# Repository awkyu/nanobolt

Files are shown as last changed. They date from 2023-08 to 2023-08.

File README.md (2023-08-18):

# nanobolt
This project is a proposal for the design of an ablation probe for osteoid osteoma using a new ablation technique proposed by Pavitra Krishnaswamy, Andras Kuthi, P. Thomas Vernier, and Martin A. Gundersen [[1]](https://doi.org/10.1109/TDEI.2007.4286518).

Surgical resection and thermal ablation techniques have been shown to have suboptimal efficacy for the treatment of osteoid osteomas due to the high risk of complications and large ablation zones. Ablation technologies that utilize electric fields instead of thermal energy to produce nanosized pores in tumor cell membranes have been shown to be an attractive method for treating a wide variety of cancers due to the short ablation times and non-invasive nature of the procedure. We propose a nanosecond pulse electric field ablation system utilizing a pulse generator as a compact solution to ablate osteoid osteomas without harming the healthy bone, leading to reduced instances of post-operative complications. 

[1] P. Krishnaswamy, A. Kuthi, P. T. Vernier and M. A. Gundersen, "Compact Subnanosecond Pulse Generator Using Avalanche Transistors for Cell Electroperturbation Studies," IEEE Transactions on Dielectrics and Electrical Insulation, vol. 14, no. 4, pp. 873-877, Aug. 2007, doi: 10.1109/TDEI.2007.4286518.

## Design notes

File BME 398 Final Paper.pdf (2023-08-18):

Abstract — Surgical resection and thermal ablation techniques have been shown to have suboptimal efficacy for the treatment of osteoid osteomas due to the high risk of complications and large ablation zones. Ablation technologies that utilize electric fields instead of thermal energy to produce nanosized pores in tumor cell membranes have been shown to be an attractive method for treating a wide variety of cancers due to the short ablation times and noninvasive nature of the procedure. We propose a nanosecond pulse electric field ablation system utilizing a pulse generator as a compact solution to ablate osteoid osteomas without harming the healthy bone, leading to reduced instances of post-operative complications.

Clinical Relevance — This establishes the efficacy of nanosecond pulse electric field ablation to ensure complete nidus ablation.

INTRODUCTION
Osteoid osteomas are small, benign bone tumors typically found in adolescents that cause pain and discomfort. The standard of care for treating osteoid osteomas has been surgical resection. Although surgical resection has been shown to have success rates of 88%-97% in removing osteoid osteomas, these procedures have a high rate of complications (20-45%) including hematoma, infection, and avascular necrosis [0, 1]. Additionally, surgically induced bone defects can increase the risk of fracture [2, 3, 4].

Minimally-invasive ablation techniques have been implemented to treat osteoid osteomas, as these techniques have been proven to cause fewer postoperative complications than conventional surgical excision [2]. Currently, radiofrequency ablation is the most common thermal ablation treatment for osteoid osteomas due to its wide availability, short postprocedural hospitalization, and ablation zone of 3-4cm [2]. Alternatively, microwave ablation has been shown to have faster ablation time and deeper tissue penetration. This is not without drawbacks. With the average nidus size of approximately 1 cm, the microwave ablation zone of 5-7 cm poses the risk of causing thermal damage to non-target tissues. This collateral damage proves to be a major drawback of microwave ablation for the treatment of osteoid osteoma [2]. In a preliminary study, Fan et al. used microwave ablation for the treatment of malignant bone tumors with a 74% success rate [5]. However, complications such as fracture, local recurrence, and infection still arose in the study, likely due to thermal damage to the surrounding healthy tissue. While radiofrequency and microwave ablation have various benefits for treating osteoid osteomas, other energy types may provide these same benefits of ablation time and tissue penetration while also limiting the ablation zone.

More recently, non-thermal ablation technologies have been investigated for tumor ablation that utilize electric fields rather than thermal energy. Irreversible electroporation (IRE) delivers low electric fields (low kV/cm) in pulses with durations of milliseconds or microseconds. The electric energy creates pores in the cell membranes of the tumor cells which disrupts ionic gradients, eventually causing the cell to die from necrosis [6]. Nanosecond pulse electric field (nsPEF) ablation uses a similar technique but with higher electric fields (tens of kV/cm) with a
nanosecond duration. The advantage of nsPEF ablation over IRE is that nsPEF ablation creates pores in both the plasma membranes as well as intracellular membranes, resulting in a phenomenon known as supra-electroporation [6]. Several studies have shown how this supra-electroporation leads to the induction of apoptosis and DNA damage [6, 7, 8]. Compared to other ablation techniques, nsPEF ablation is more time-efficient as only 100 pulses are needed to effectively destroy the tumor [6, 7]. The ability of nsPEF to rapidly induce cell death noninvasively without the use of heat or chemicals makes it an attractive treatment option for a plethora of cancers.

While the literature has shown that nsPEF ablation has been successful in treating a variety of tumors, it has not been extensively researched for the ablation of osteoid osteoma. This study aims to address this gap in knowledge and proposes a nanosecond pulse generator that will be used to induce supra-electroporation in osteoid osteomas. The nanosecond pulse generator will be used in combination with a custom probe, and both of these components will comprise the entire nanosecond pulse electric field ablation system. By using a novel power generator, this solution will target osteoid osteomas with more precision, limiting collateral damage to surrounding bone or tissue.

For this preliminary study, only the pulse generator was verified as the probe design is still being perfected. Testing the new nanosecond pulse generator in silico using Multisim software demonstrates a pulse with a magnitude of approximately 2 V is produced. While other nanosecond pulse generators can produce pulses with a voltage greater than 1 kV, this study still offers verification that the simplified circuit used in this study produces pulses of electrical energy. This provides the confidence needed to further develop the project by building upon the current circuit design to achieve the voltages required for effective ablation. Future studies should be conducted to further verify the circuit design as well as the probe before validating the entire ablation system by assessing its feasibility in vivo for the removal of osteoid osteomas. METHODS

Multisim software was used to simulate the circuit needed for the nanosecond pulse generator. In a paper published by Krishnaswamy et al., a detailed schematic is provided for an avalanche pulse generator circuit which served as the inspiration for this study [9]. Using the avalanche pulse generator circuit as a starting point, this study aimed to first simulate the findings of Krishnaswamy et al., and then alter key parameters to change the output characteristics of the circuit. The circuit model used in the Multisim simulation was assembled as seen in figure 1. The DC power supply block, which consisted of a 8-14.5 VDC power supply followed by a DC-DC converter, was simplified as a 2.5 kV voltage source in the simulation. The transformer was modeled with no leakage inductance or resistance; the core was modeled as non-ideal with a flux of 250uWb * tanh(.2*i) where “i” was the magnetizing inductance current. The Bipolar Junction Transistor (BJT) NPN transistor was used to model the avalanche transistor. This transistor provided a conservative estimate of the circuit as it lacked the quick response of the avalanche transistors. The rise time of the trigger source was specified as 0.5 nanoseconds and varying levels of voltages were applied to assess the impact of the voltage on the output waveform. Peak voltage and rise time of the waveform were analyzed using a transient analysis with a step time of 0.1 nanoseconds.

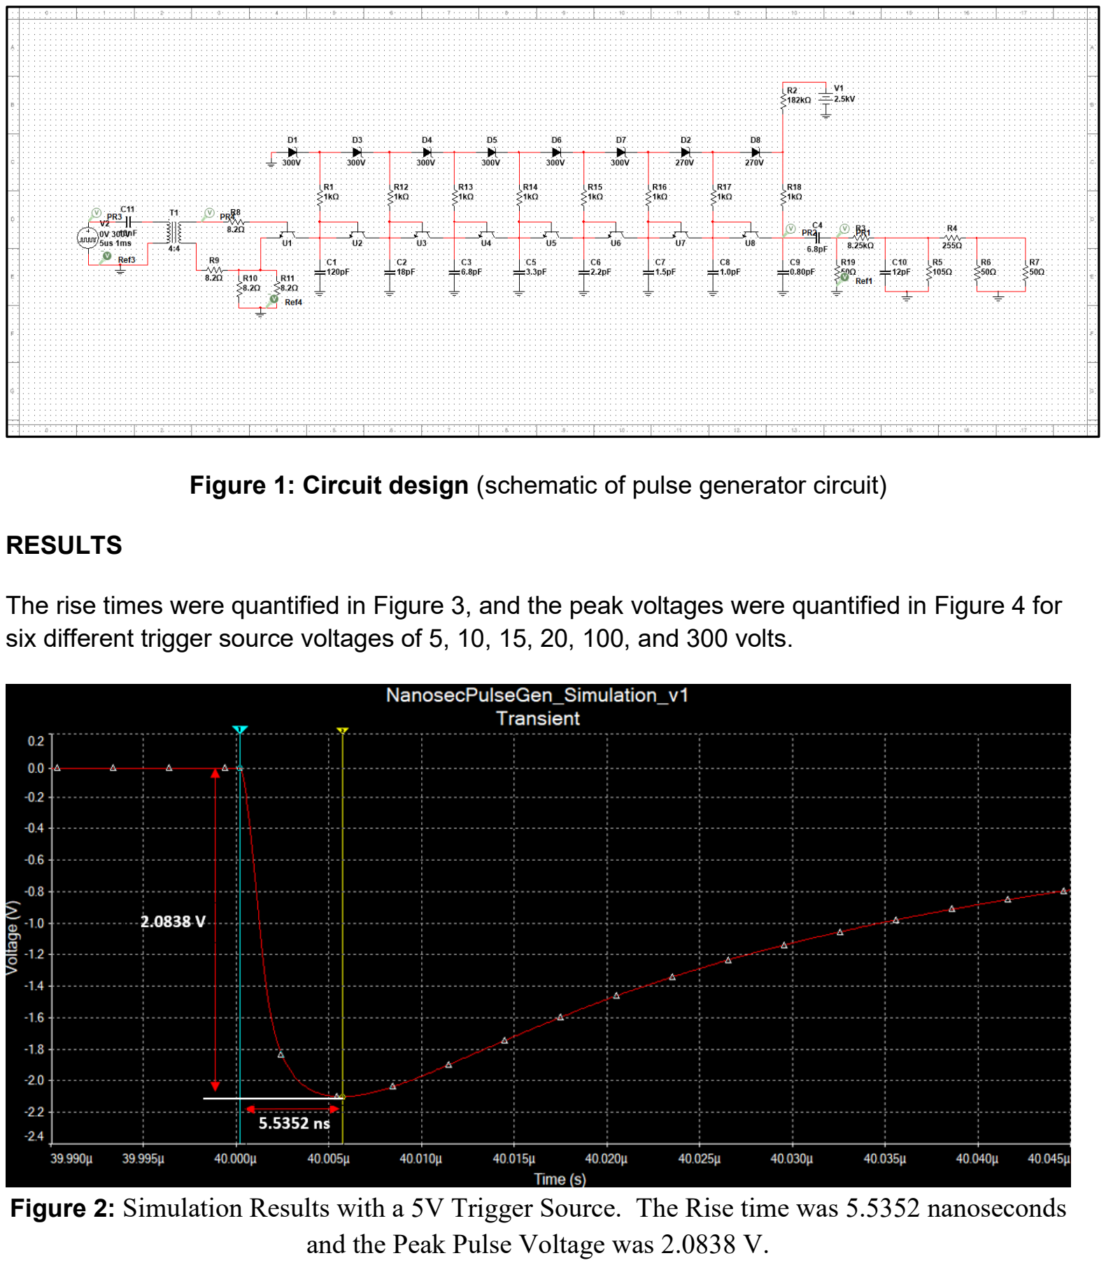
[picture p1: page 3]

Figure 1: Circuit design (schematic of pulse generator circuit) RESULTS

The rise times were quantified in Figure 3, and the peak voltages were quantified in Figure 4 for six different trigger source voltages of 5, 10, 15, 20, 100, and 300 volts.

Figure 2: Simulation Results with a 5V Trigger Source. The Rise time was 5.5352 nanoseconds and the Peak Pulse Voltage was 2.0838 V.

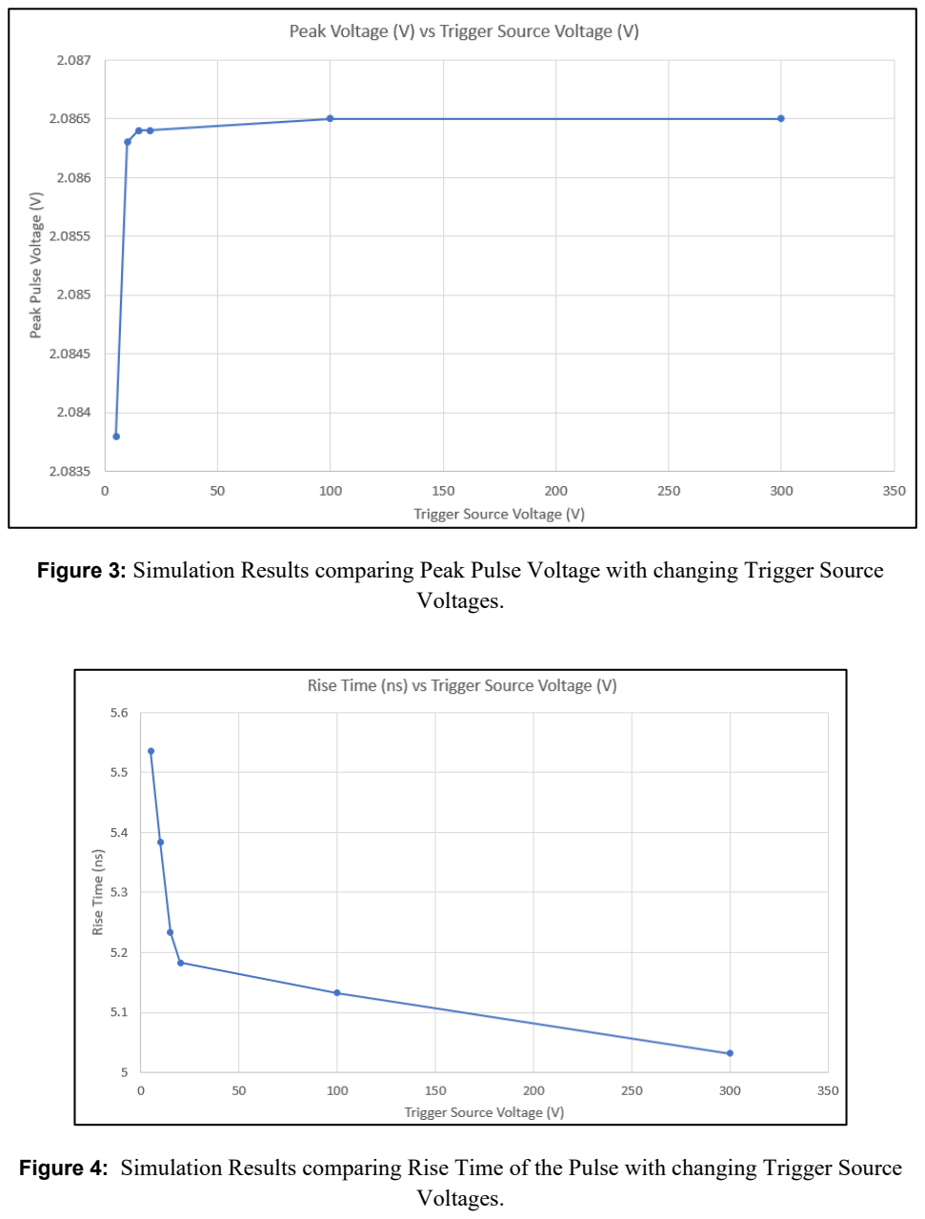
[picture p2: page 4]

Figure 3: Simulation Results comparing Peak Pulse Voltage with changing Trigger Source Voltages.

Figure 4: Simulation Results comparing Rise Time of the Pulse with changing Trigger Source Voltages.

DISCUSSION

In Figure 2, the output signal was shown in the time-domain with a single trigger source voltage of 5 volts. This output signal showed promising results in that it had the shape of a pulse that could be used in electroporation applications. However, the voltage magnitude was roughly a thousandth of the desired value [9]. This decreased magnitude would render the device useless in electroporation applications. However, further modification of the simulation could lead to a more appropriate waveform for the generator’s intended use. Additionally, a prototype of the generator could be assembled and the output voltage could be assessed to compare results with the simulation. While this would have a cost associated with it, the testing may reveal limitations of the Multisim simulation software.

According to Figure 3, the peak voltage approached a horizontal asymptote at around 2 volts with an increasing trigger source voltage. These peak voltage values deviated from normal kilovolt values for the peak voltage in similar ablation technologies by orders of magnitude. On the other hand, rise times of around 5 nanoseconds (see Figure 4) were very plausible and much lower than millisecond to microsecond rise times in similar technologies. In order to improve the rise times to the subnanosecond range in future simulations, avalanche transistors could be used instead of ideal transistors.

There were a number of limitations in this study that hindered the results. First, this study was restricted to a simulated environment, which idealized many components to a form that was not indicative of their real-world state. Second, this study was limited to a short 15-week period of clinical research, needs statement identification and selection, finally followed with experimental design and performance. With additional time in the future, this study would be able to put together a real world model of the pulse generator.

Although this study found rather low peak pulse voltages, the overall nature of these pulses still offered verification for the treatment of osteoid osteomas with nanosecond pulse electric field ablation technologies. This study was able to produce pulses with short rise times, which was a key waveform characteristic when evaluating a pulse generator for its capability of treating osteoid osteomas via ablation.
CONCLUSION

This study aimed to test a new nanosecond pulse generator in silico with Multisim software to produce a pulse capable of powering an ablation probe utilizing a simplified circuit design. Although the resulting voltage magnitude was approximately a thousandth of the desired value, the output signal had the shape of a signal used in electroporation applications. With further modification of the schematic design of the circuit, the design shows promise in achieving a desirable waveform for the intended application. A prototype of the generator could also be fabricated and further tested to analyze the output voltage. This testing would reveal and mitigate the limitations of the in silico experiment. In addition to the verification of the variability in power of the circuit design, future studies could focus on the verification and validation of the efficiency of the circuit. Using Multisim or electromagnetic simulation, the circuit could be modified to operate between 915 MHz and 2450 MHz in order to have an ablation time of less than 10 minutes. The results of this study provides confidence in accurate modification of the circuit design to produce desired output signals and pulse magnitudes for use in the treatment of osteoid osteomas. Future studies should test the pulse generator with the ablation probe on an ex vivo tissue sample to analyze the effectiveness of the ablation technology on osteoid osteomas.

References

[0] C. Neyisci, Y. Erdem, “Safe and Effective Treatment Choice for Osteoid Osteoma: Computed Tomography-guided Percutaneous Radiofrequency Ablation,” Cureus vol. 11, no. 8. pp. e5526, Aug. 2019. Accessed on: Apr. 21, 2021. [Online]. Available doi: 10.7759/cureus.5526
[1] Y. Oc, B. E. Kilinc, S. Cennet, M. M. Boyacioglu, R. Ertugrul, and A. Varol, “Complications of Computer Tomography Assisted Radiofrequency Ablation in the Treatment of Osteoid Osteoma,” BioMed Research International, vol. 2019, pp. 1–6, May 2019, doi: 10.1155/2019/4376851.
[2] “Thermal Ablation of Osteoid Osteoma: Overview and Step-by-Step Guide,” RadioGraphics, vol. 29, pp. 2127-2141, Nov. 2009. Accessed on: Mar. 3, 2021. [Online]. Available doi: 10.1148/rg.297095081
[3] D. I. Rosenthal, F. J. Hornicek, M. W. Wolfe, L. C. Jennings, M. C. Gebhardt, H. J. Mankin, “Percutaneous Radiofrequency Coagulation of Osteoid Osteoma Compared with Operative Treatment,” The Journal of Bone and Joint Surgery, vol. 80, no. 6, pp. 815-821, June 1998. Accessed on: Mar. 7, 2021. [Online]. Available doi: 10.2106/00004623-199806000-00005
[4] Z. G. Papathanassiou, P. Megas, T. Petsas, D. J. Papachristou, J. Nilas, D. Siablis, “Osteoid Osteoma: Diagnosis and Treatment,” Orthopedics, vol. 11, no. 31, pp. 1118-1127, Nov. 2008. Accessed on: Mar. 7, 2021. [Online]. Available doi: 10.3928/01477447-20081101-20
[5] Q. Fan, B. Ma, Y. Zhou, M. Zhang, X. Hao, “Bone tumors of the extremities or pelvis treated by microwave-induced hyperthermia,” Clinical orthopaedics and related research, no. 406, 2015. Accessed on: Mar. 7, 2021. [Online]. Available doi: 10.1097/01.blo.0000037439.23683.9c
[6] S. Beebe, N. Sain, and W. Ren, “Induction of Cell Death Mechanisms and Apoptosis by Nanosecond Pulsed Electric Fields (nsPEFs),” Cells, vol. 2, no. 1, pp. 136–162, Mar. 2013, doi: 10.3390/cells2010136.
[7] X. Chen, J. F. Kolb, R. J. Swanson, K. H. Schoenbach, and S. J. Beebe, “Apoptosis initiation and angiogenesis inhibition: melanoma targets for nanosecond pulsed electric fields,” Pigment Cell & Melanoma Research, vol. 23, no. 4, pp. 554–563, Apr. 2010, doi: 10.1111/j.1755-148x.2010.00704.x.
[8] T. Koga, K. Morotomi-Yano, T. Sakugawa, H. Saitoh, and K. Yano, “Nanosecond pulsed electric fields induce extracellular release of chromosomal DNA and histone citrullination in neutrophil-differentiated HL-60 cells,” Scientific Reports, vol. 9, no. 1, Jun. 2019, doi: 10.1038/s41598-019-44817-9.
[9] P. Krishnaswamy, A. Kuthi, P. T. Vernier and M. A. Gundersen, "Compact Subnanosecond Pulse Generator Using Avalanche Transistors for Cell Electroperturbation Studies," IEEE Transactions on Dielectrics and Electrical Insulation, vol. 14, no. 4, pp. 873-877, Aug. 2007, doi: 10.1109/TDEI.2007.4286518.

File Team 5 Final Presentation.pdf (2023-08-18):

# REdesign Lab

# Team 5: NanoBolt™

# Bevin Neill, Jefferson Bercaw, Mattie Mckee, Alex Kyu, and Drew DiSerafino

# Clinical Problem

# - Osteoid Osteomas

# - Small benign bone tumors - Typically affect children and young adults - Account for 11% of all benign bone tumors (~450,000 cases per year) - Cause pain and discomfort

# - Current Solutions

# - Surgical Resection

# - High risk of complications - Increased risk of fracture

# - Thermal Ablation

# - Microwave or radiofrequency - Ablation zone size of 5-7 cm - Average size of osteoid osteoma = 1-2 cm - Increased risk of damage to healthy bone

https://www.youtube.com/watch?v=gGn3XhZBSQA

https://www.jnjmedicaldevices.com/en-US/product-family/neuwave-microwave-ablation-systems

A. Julka, P. Jebson, and M. Tomaino, “Common Benign Tumors of the Hand,” AAOS, Aug. 2015. https://www5.aaos.org/OKOJ/vol13/issue8/HAN055/?ssopc=1

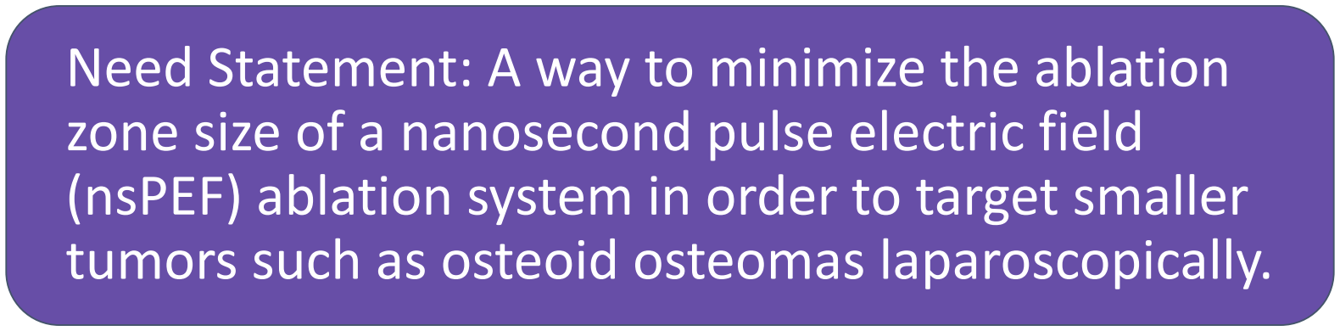
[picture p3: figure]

# Need Statement: A way to minimize the ablation zone size of a nanosecond pulse electric field (nsPEF) ablation system in order to target smaller

tumors such as osteoid osteomas laparoscopically.

# Lab Market and FDA Regulation

# TAM: Total US Bone Tumor Population

# SAM: Benign bone tumor cases

# Target: Osteoid osteoma cases

# Market Size: ~450,000 * $1,940/patient = $873,000,000

# Value Proposition: Lower Ablation Zone and novel application

# Product Code: NEY

# Regulation Number: 878.4400

# Regulatory Pathway: Class 2, 510(k)

# Estimated Individuals with Bone Tumors Population in US

(18,150,000 = ~5.5%)

# Malignant tumors

~77.1%

# Benign bone tumors

(4,148,571 = ~22.9%)

# Osteoid osteoma

11% or 456,342

G. R. Gaumer, D. S. Weinberg, C. D. Collier, P. J. Getty, and R. W. Liu, “An Osteological Study on the Prevalence of Osteochondromas,” The Iowa orthopaedic journal, vol. 37, pp. 147–150, 2017, Accessed: Feb. 23, 2021. [Online]. Available: https://www.ncbi.nlm.nih.gov/pmc/articles/PMC5508295/
S. Noordin et al., “Osteoid osteoma: Contemporary management,” Orthopedic Reviews, vol. 10, no. 3, Sep. 2018, doi: 10.4081/or.2018.7496.
S. A. Astani, M. L. Brown, and K. Steusloff, “Comparison of Procedure Costs of Various Percutaneous Tumor Ablation Modalities,” The Association for Medical Imaging Management, Aug 2014, Accessed: Feb. 23, 2021. [Online]. Available: http://www.ahra.org/AM/Downloads/OI/qc/RM364_p12-17_Features.pdf

# Traceability Matrix

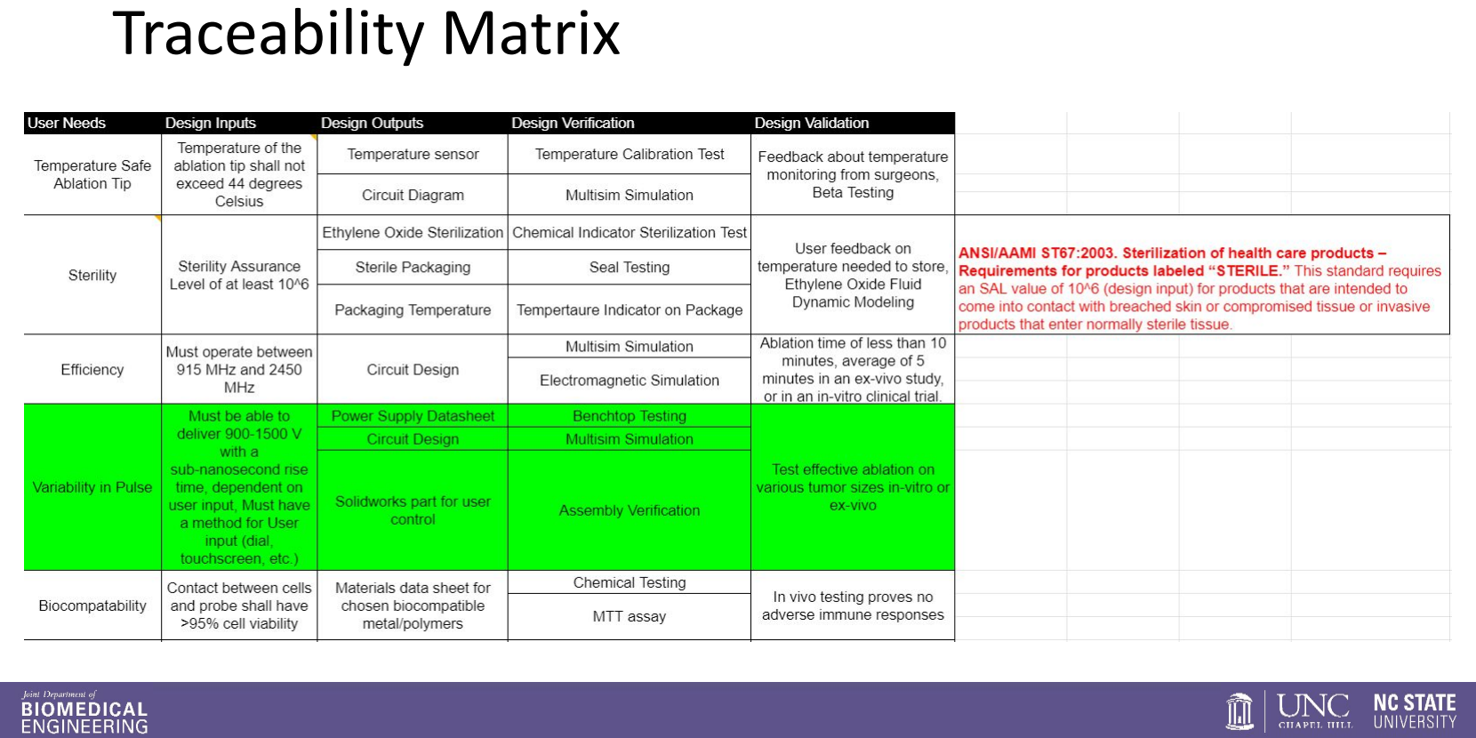
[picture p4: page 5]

# Traceability Matrix (Continued)

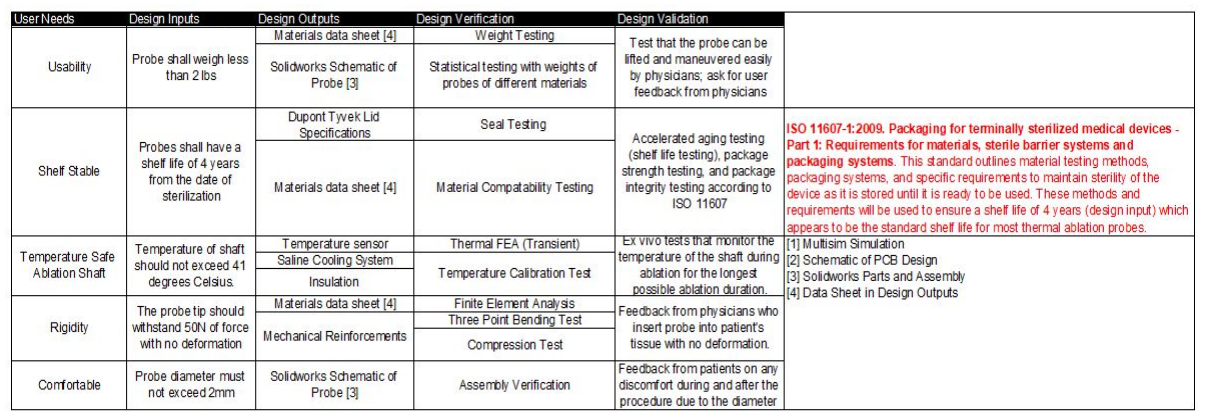
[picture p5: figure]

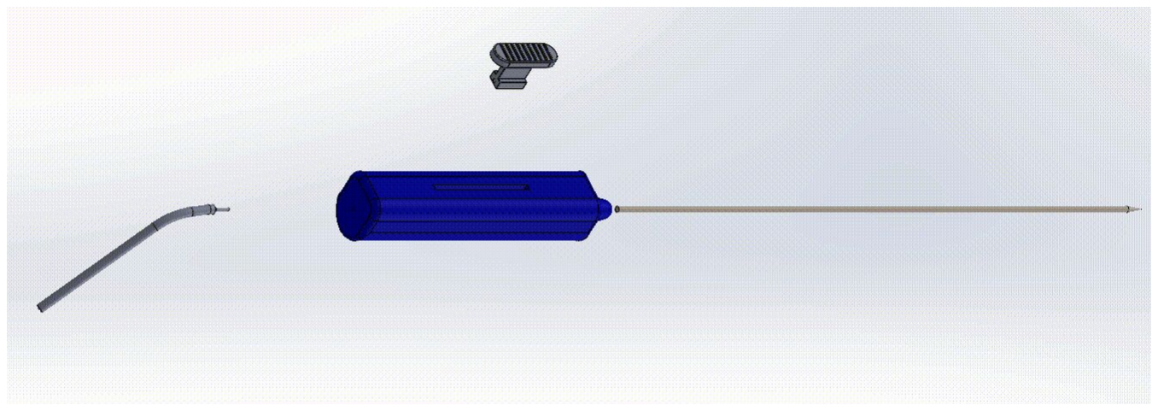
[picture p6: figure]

# Solution

# - Nanosecond Pulse Electric Field (nsPEF) Ablation

# - High-intensity pulsed electric fields with a nanosecond pulse duration - Creates pores in both the plasma membrane and intracellular membrane

# - Induce apoptosis in tumor cells

# - Subnanosecond Pulse Generator - creates pulses of electrical energy - Probe - application of electric field to tumor - Thumb Tab - control depth of insertion - Insulator - protect surrounding tissue

| Component | Cost
PCB Materials* | $ 420.33
Metal Probe | $ 6.99
Thumb Tab | $ 9.99
Handle | $ 9.99
Custom Wire | $ 6.99
Insulator | $ 17.99
Total | $ 472.28

# Bill of Materials

# * see Appendix A

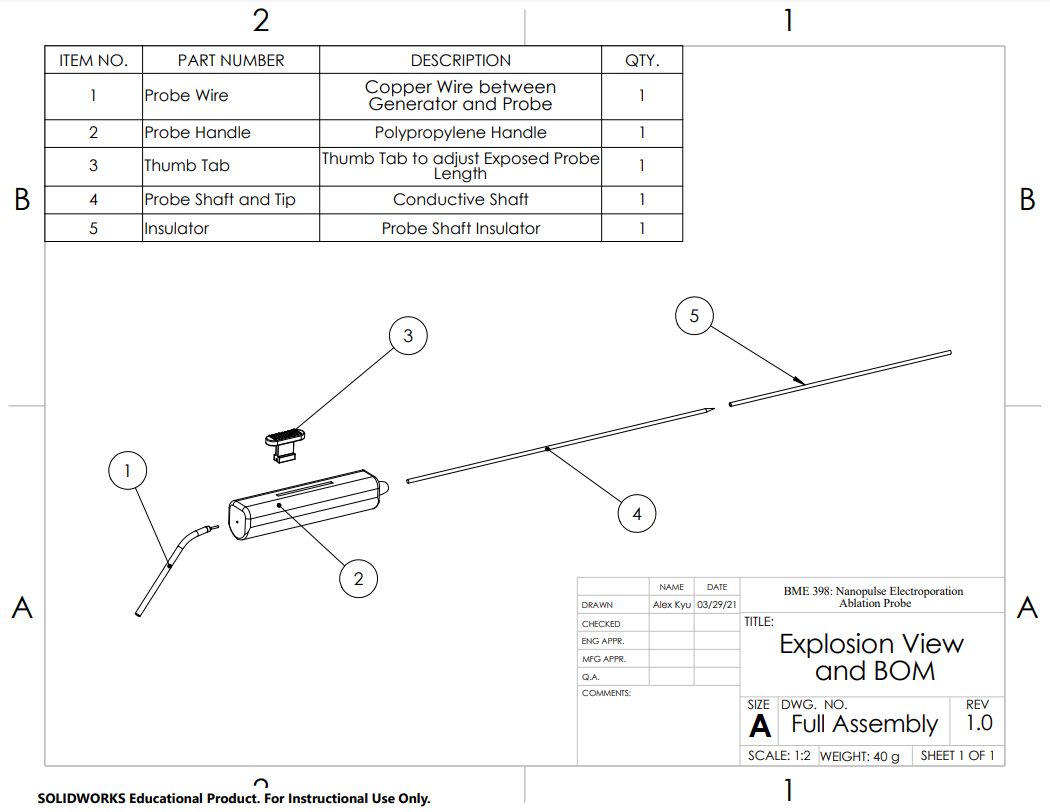
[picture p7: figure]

# Lab Manufacturing Methods

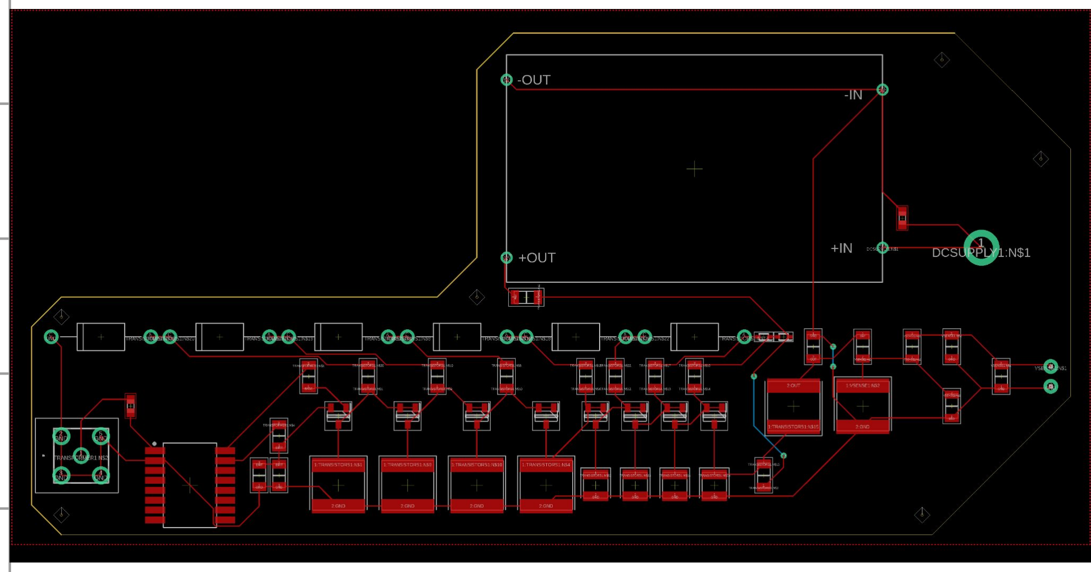
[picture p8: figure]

Part | Supplier/Manufacturer | Material
Plastic Handle | Injection Molding | Polypropylene
Insulator | Insulon® Sheaths | Stainless Steel
Probe | Lathe | Stainless Steel
Wire | Y.C. Cable® | Multiple

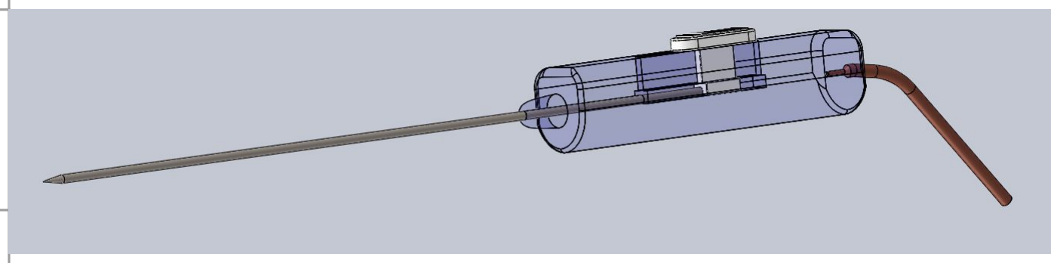
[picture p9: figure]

Thumb Probe Adjustor | Injection Molding | Polypropylene
Generator | JLCPCB® | PCB

# DFM Principles

# Principles used in our design:

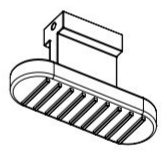
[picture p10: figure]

# a. Largest Acceptable Tolerances (outer portion of handle) b. Available Manufacturing Techniques in the Fab Lab c. Geometry (Cylinders!) Possible areas of improvement: a. Poka Yoke (Thumb Tab) b. Singular Axis of Assembly (Divide handle)

# Verification/Validation

# Multisim Simulation of Power Generator Circuit

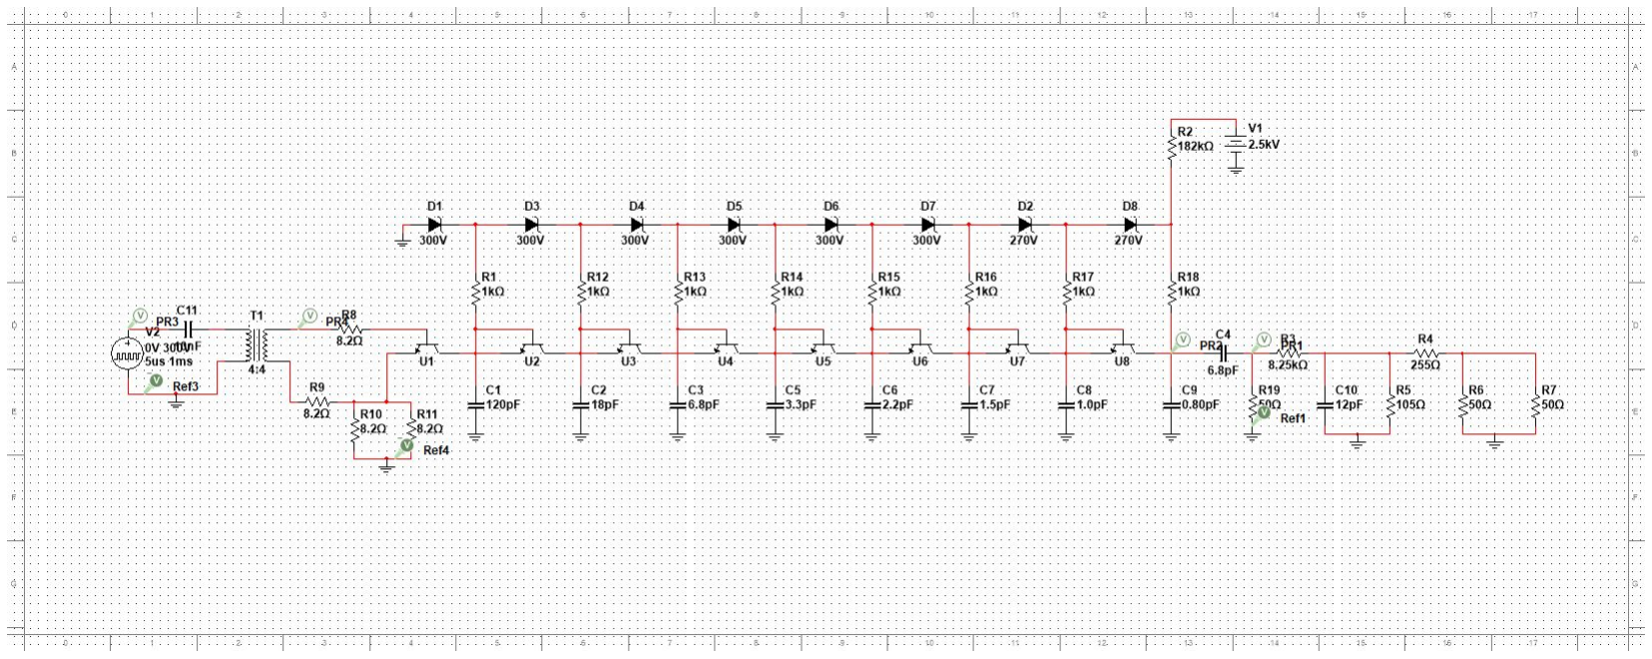
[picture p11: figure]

T. Koga, K. Morotomi-Yano, T. Sakugawa, H. Saitoh, and K. Yano, “Nanosecond pulsed electric fields induce extracellular release of chromosomal DNA and histone citrullination in neutrophil-differentiated HL-60 cells,” Scientific Reports, vol. 9, no. 1, Jun. 2019, doi: 10.1038/s41598-019-44817-9.

# Verification/Validation

# User Need: Variability in Pulse time

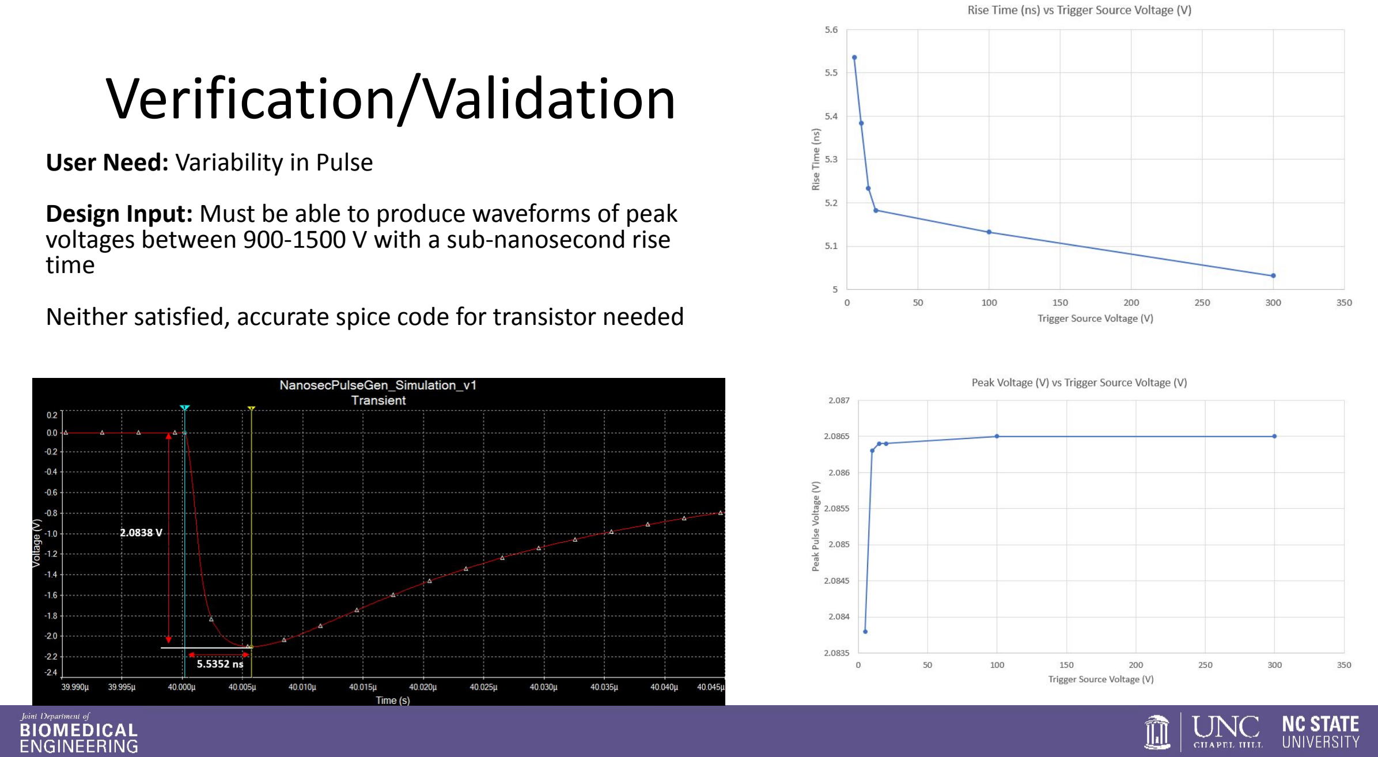
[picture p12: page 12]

# Design Input: Must be able to produce waveforms of peak voltages between 900-1500 V with a sub-nanosecond rise

# Neither satisfied, accurate spice code for transistor needed

# Project Analysis and Future

# - Future studies:

# - Prototype generator to analyze output voltage - Test the pulse generator with the ablation probe on an ex vivo tissue sample - Will likely need to raise additional funds for project (estimated prototype cost

$472.28)

# - Timeline is achievable, although will be tight

# - Risks

# - Overall Success

# - Generator not producing desired output waveform - Financial Risk: expensive prototype

# - User Harms

# - Leakage Current - Electric Field produced too large - Detached thumb tab - Misinterpretation of user interface to set ablation power

# - Continuing For Senior Design

# - Solution meets unmet clinical need with a large market size - Design is feasible to manufacture, especially using Fab Lab

# Questions?

Appendix A - Full PCB BOM Part Name | Unique Identifying Number | Description | Quantity | Material | Vendor | Unit Cost | Total Cost
Avalanche Transistor | TR1 | Avalanche Transistor | 8 | n/a | Mouser | $9.73 | $77.84
DC-DC Converter | CONV1 | DC-DC Converter | 1 | n/a | PicoElectronics | $136.24 | $136.24
Resistors (1K) | R1 | Resistors (1K) | 8 | n/a | Mouser | $1.25 | $10.00
Resistors (8) | R2 | Resistors (8) | 4 | n/a | Mouser | $0.46 | $1.84
Resistors (181K) | R3 | Resistors (181K) | 1 | n/a | Mouser | $0.10 | $0.10
Resistors (50) | R4 | Resistors (50) | 1 | n/a | Mouser | $1.62 | $1.62
Resistors (8.5k) | R5 | Resistors (8.5k) | 1 | n/a | Mouser | $0.10 | $0.10
Resistors (255) | R6 | Resistors (255) | 1 | n/a | Mouser | $0.10 | $0.10
Resistors (105) | R7 | Resistors (105) | 1 | n/a | Mouser | $0.10 | $0.10
Capacitor (120p) | C1 | Capacitor (120p) | 1 | n/a | Digikey | $21.32 | $21.32
Capacitor (18p) | C2 | Capacitor (18p) | 1 | n/a | Digikey | $14.34 | $14.34
Capacitor (6.8p) | C3 | Capacitor (6.8p) | 2 | n/a | Digikey | $14.34 | $28.68
Capacitor (3.3p) | C4 | Capacitor (3.3p) | 1 | n/a | Digikey | $15.50 | $15.50
Capacitor (2.2p) | C5 | Capacitor (2.2p) | 1 | n/a | Digikey | $1.50 | $1.50
Capacitor (1.5p) | C6 | Capacitor (1.5p) | 1 | n/a | Digikey | $1.50 | $1.50
Capacitor (1.0p) | C7 | Capacitor (1.0p) | 1 | n/a | Digikey | $1.50 | $1.50
Capacitor (0.8p) | C8 | Capacitor (0.8p) | 1 | n/a | Digikey | $0.80 | $0.80
Capacitor (12p) | C9 | Capacitor (12p) | 1 | n/a | Digikey | $14.34 | $14.34
Capacitor (0.1u) | C10 | Capacitor (0.1u) | 1 | n/a | Sparkfun | $0.95 | $0.95
Capacitor (10n/0.01u) | C11 | Capacitor (10n/0.01u) | 1 | n/a | Sparkfun | $0.95 | $0.95
Zener Diode (300 V) | D1 | Zener Diode (300 V) | 6 | n/a | Mouser | $12.67 | $76.02
Zener Diode (270 V) | D2 | Zener Diode (270 V) | 2 | n/a | Mouser | $0.30 | $0.60
SMA Connector | J1 | SMA Connector | 1 | n/a | Mouser | $3.07 | $3.07
Transformer | T1 | Transformer | 1 | n/a | Digikey | $3.92 | $3.92
PCB | PCB1 | Printed Circuit Board | 1 | n/a | JLCPCB | $7.40 | $7.40
| | | | | | Total | $420.33

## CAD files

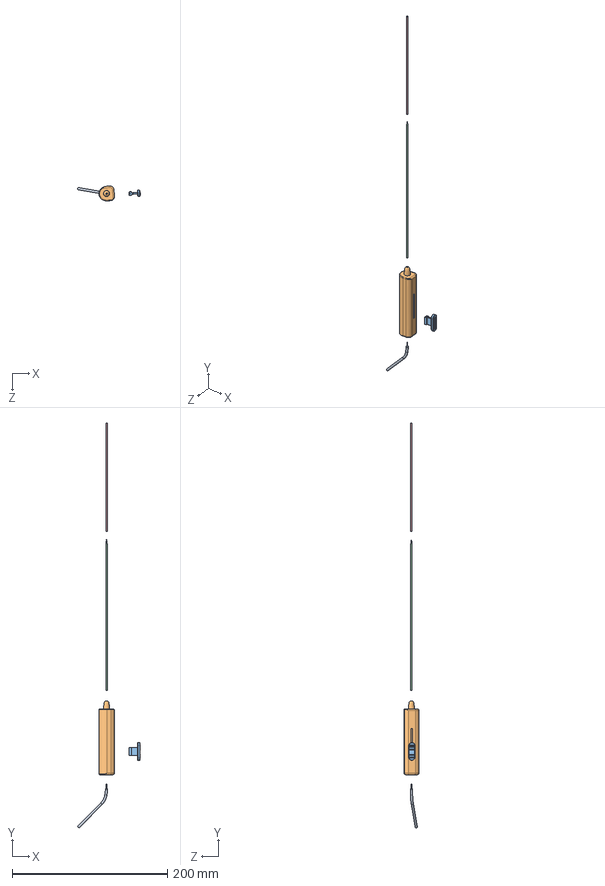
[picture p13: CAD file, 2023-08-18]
Mechanical Design/Part_Assembly/groupAssembly.SLDASM
81.1 x 522.5 x 19.2 mm
wire
handle
thumbTab
tippytip_and_shaft
insulator

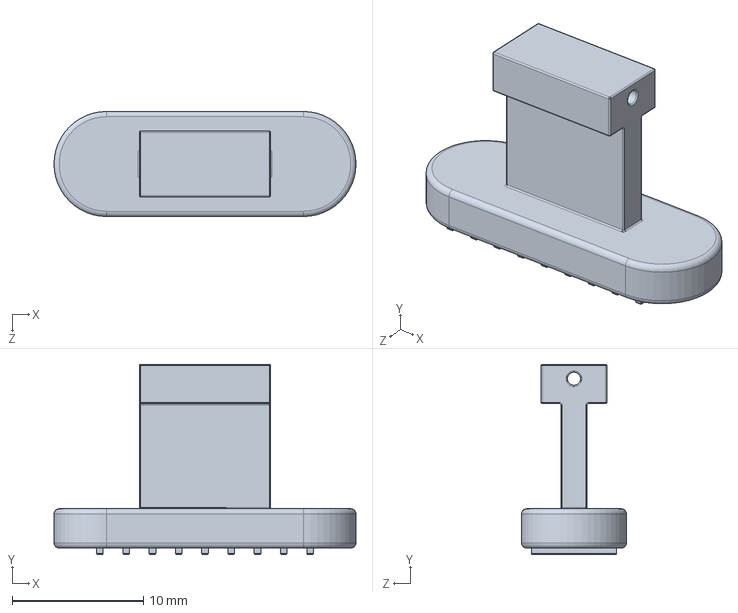
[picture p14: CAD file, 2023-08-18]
Mechanical Design/Part_Assembly/thumbTab.SLDPRT
23.0 x 14.5 x 8.00 mm

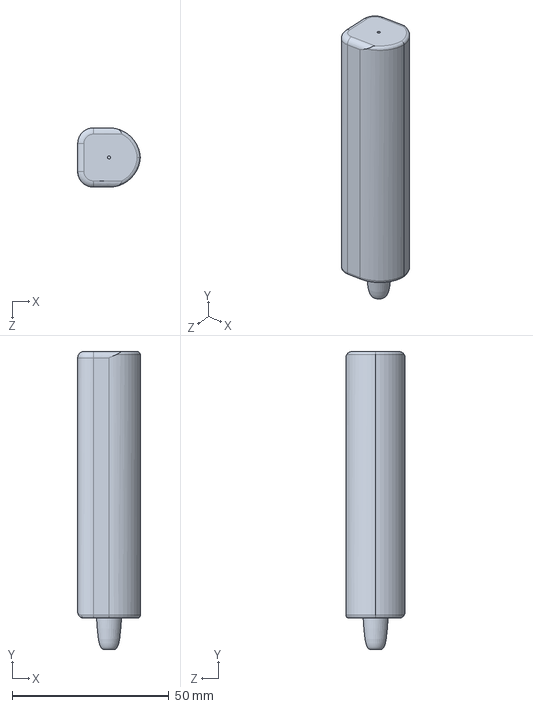
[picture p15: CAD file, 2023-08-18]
Mechanical Design/Part_Assembly/handle.SLDPRT
20.0 x 95.0 x 18.9 mm

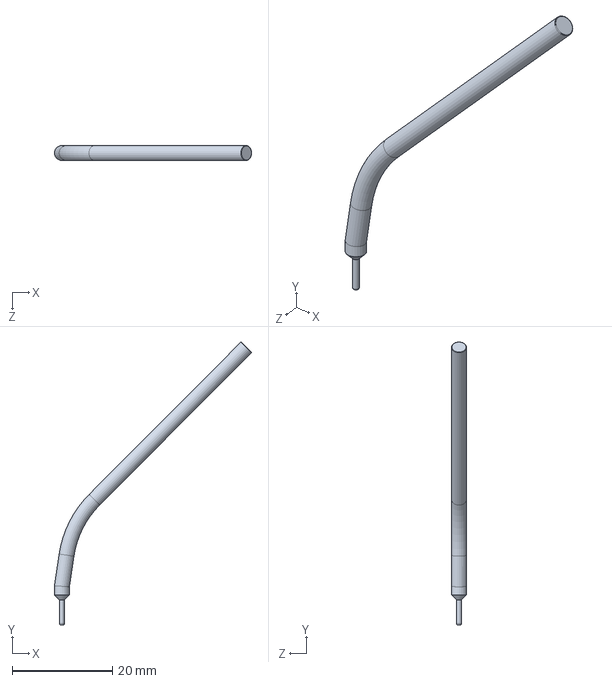
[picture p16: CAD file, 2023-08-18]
Mechanical Design/Part_Assembly/wire.SLDPRT
39.4 x 56.6 x 3.00 mm

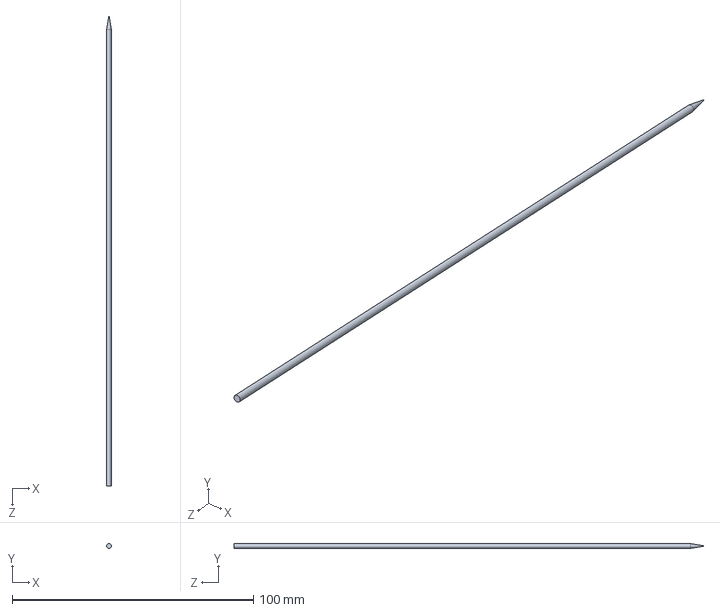
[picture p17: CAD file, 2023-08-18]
Mechanical Design/Part_Assembly/tippytip_and_shaft.SLDPRT
2.00 x 2.00 x 195.0 mm

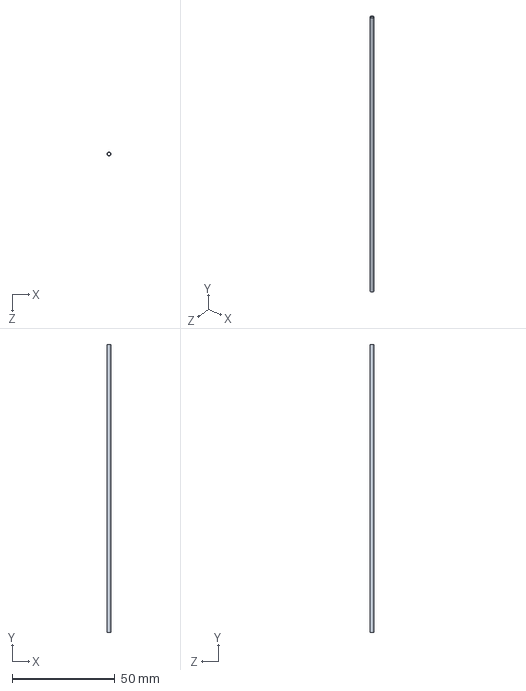
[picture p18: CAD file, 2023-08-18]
Mechanical Design/Part_Assembly/insulator.SLDPRT
2.00 x 140.0 x 2.00 mm

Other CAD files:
Mechanical Design/Part_Assembly/groupAssembly.SLDDRW
Mechanical Design/Part_Assembly/thumbTab.SLDDRW

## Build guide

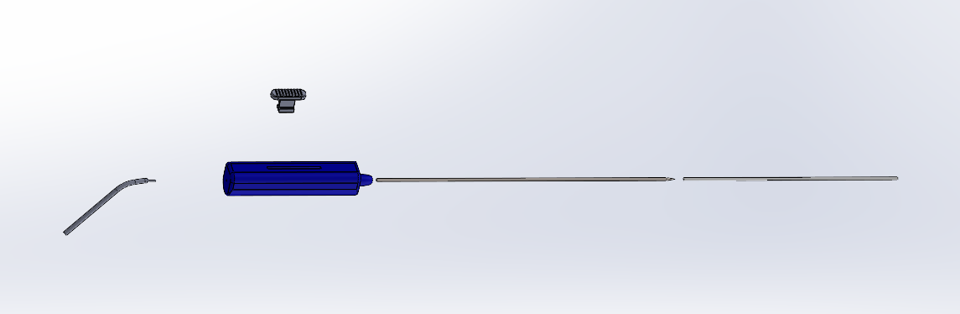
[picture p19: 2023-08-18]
Mechanical Design/Part_Assembly/Screenshot 2021-03-28 145811.png

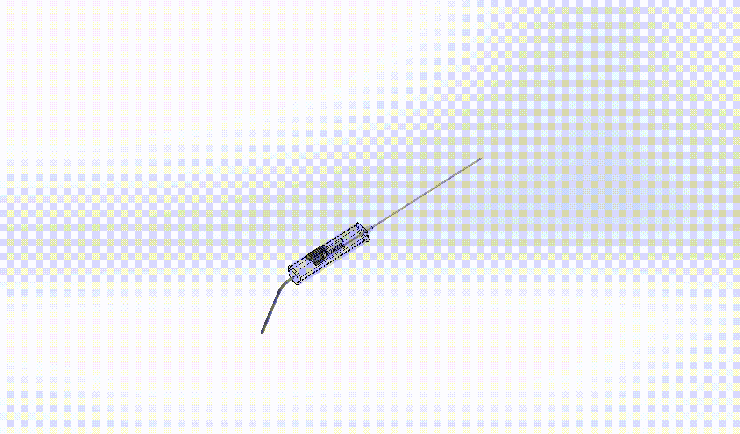
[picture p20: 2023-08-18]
Mechanical Design/Part_Assembly/groupAssembly.gif

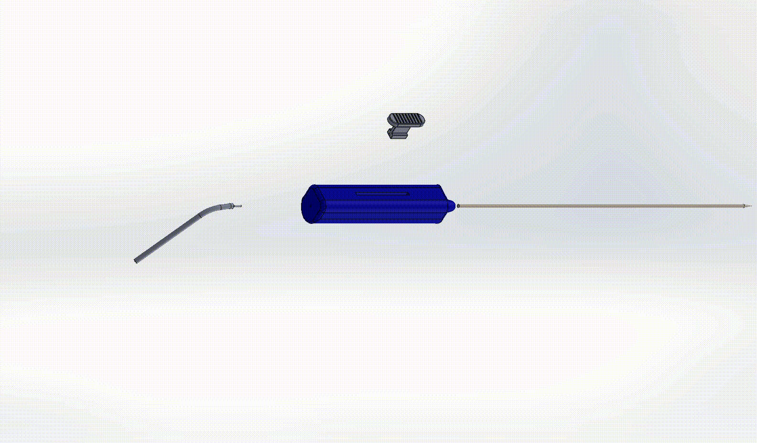
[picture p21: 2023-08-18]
Mechanical Design/Part_Assembly/groupAssembly_collapse.gif

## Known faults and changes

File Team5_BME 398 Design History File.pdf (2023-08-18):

BME 398 Design History File

Jefferson Bercaw, Drew Diserafino, Alex Kyu, Mattie McKee, Bevin Neill

Joint Department of Biomedical Engineering, UNC-CH and NC State

BME 398 - Biomedical Engineering Design and Manufacturing II

April 30, 2021

Traceability Matrix
Unique Identifying Number: TR1 Revision Number: 1
Page Number: 1
Acceptance Status: Accepted

Quality Engineer Signature:

Work Breakdown - contribution from each team member

All team members selected and evaluated two user needs and their associated inputs, outputs, verification, and validation. The team also came together to discuss key standards and how they applied to some of our user needs. With 10 total user needs, each group member contributed 20% to the total work.

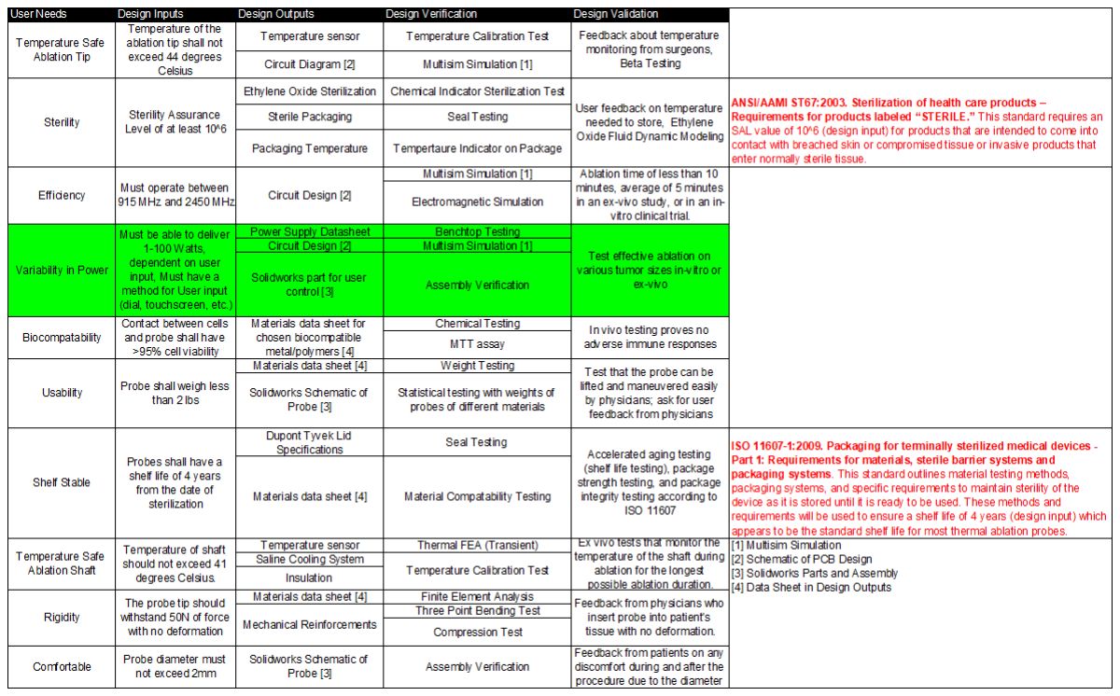
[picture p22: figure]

Risk Register
Unique Identifying Number: RR1 Revision Number: 1
Page Number: 1
Acceptance Status: Accepted

Quality Engineer Signature:

Work Breakdown - contribution from each team member

Each team member chose two hazards associated with our device and completed their associated harms, probabilities, impacts, risks, and mitigation. With 10 total hazards, each group member contributed 20% to the total work.

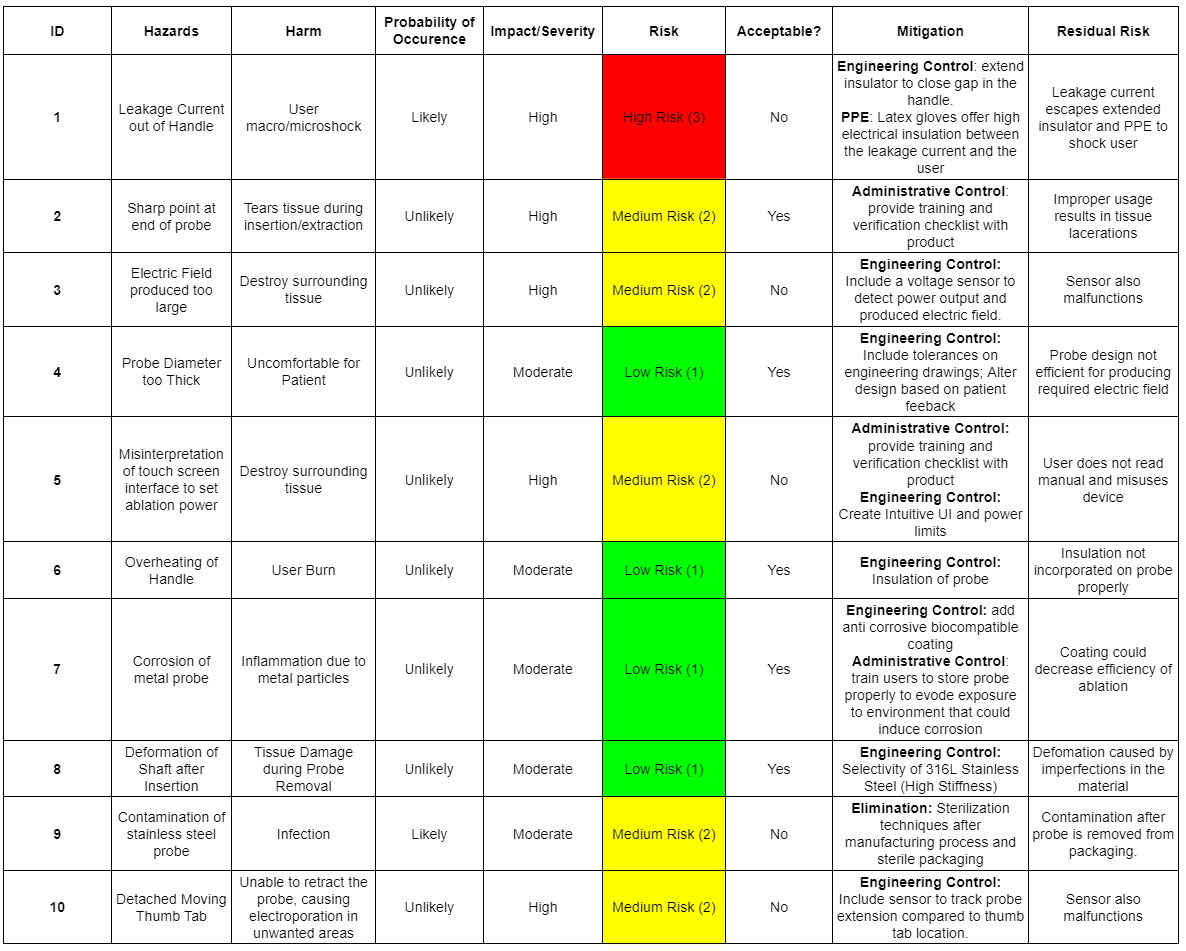
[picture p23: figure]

Design Outputs
Unique Identifying Number: DO1 Revision Number: 1
Page Number: 7
Acceptance Status: Accepted

Quality Engineer Signature:

Work Breakdown - contribution from each team member

Alex and Drew completed the Bill of Materials, Data Sheet, and PCB, providing 20% of work each.
Mattie and Bevin completed the Engineering Drawings and the Manufacturing Summary, providing 20% of work each. Jefferson completed the CNC Milling of the probe tip, providing 20% of work.

Manufacturing Summary

In order to fulfill the user need of “Variability in Power,” the nanosecond pulse electric field ablation system must be able to deliver 1-100 Watts of power which can be varied depending on the size of the specific osteoid osteoma that is being removed. The parts of the design that need to be manufactured to verify this need are the subnanosecond pulse generator and the probe. The subnanosecond pulse generator will be built using a circuit outlined in a paper by Krishnaswamy et al. which will make it reasonably easy to assemble [1]. Since this circuit design may need to be modified to meet the needs of our device, it was decided that the generator should be built rather than bought to ensure that we have a solid understanding of the circuit design. This way, we can exchange the circuit elements with confidence that the circuit will still work. The probe will also be built rather than bought since the probe is essentially a long piece of conductive material that can be easily manufactured using CNC milling which can be accomplished in the Fab Lab. This will be financially advantageous since we will only have to buy the raw materials instead of buying the entire part from an outside supplier.

The connectors to the PCB will utilize the poka yoke DFM principle so that they will not be confused. Additionally, all the components are on one side, allowing for easier scaling in manufacturing. The components are orientated in the same direction, allowing for the PCB to be produced using wave soldering. The probe design incorporates many DFM principles including the use of available manufacturing techniques, compatible materials, and optimal geometry. As aforementioned, the probe will be manufactured using CNC milling which can be accomplished using the machine in the Fab Lab or other instrument shops on campus. It will also be composed of 316 Stainless Steel which is low cost and can be CNC milled. The probe will also be quite easy to manufacture since it has a very simple and symmetrical geometry that is essentially a long cylinder with a point.

A printed circuit board (PCB) design will be chosen for the manufacturing technique for the subnanosecond generator because it is a compact solution that can be created in a short amount of time at a low cost. Since the circuit for the generator contains numerous circuit elements, the PCB will allow us to avoid “wire spaghetti” and ensure the circuit is connected properly in a neat and organized manner. CNC milling will be chosen as the manufacturing method for the probe. As previously mentioned, the probe is composed of stainless steel which is compatible with CNC milling. The probe also has a simple geometry that can easily be produced by grinding the ends of a stainless steel cylinder into a point. We also have access to a CNC milling machine through the Fab Lab and other facilities on campus which makes it an ideal manufacturing method.

Bill of Materials

Part Name | Unique Identifyin g Number | Descriptio n | Quantity | Material | Vendor | Unit Cost | Total Cost
Avalanche Transistor | TR1 | Avalanche Transistor | 8 | n/a | Mouser | $9.73 | $77.84
DC-DC Converter | CONV1 | DC-DC Converter | 1 | n/a | PicoElectro nics | $136.24 | $136.24
Resistors (1K) | R1 | Resistors (1K) | 8 | n/a | Mouser | $1.25 | $10.00
Resistors (8) | R2 | Resistors (8) | 4 | n/a | Mouser | $0.46 | $1.84
Resistors (181K) | R3 | Resistors (181K) | 1 | n/a | Mouser | $0.10 | $0.10
Resistors (50) | R4 | Resistors (50) | 1 | n/a | Mouser | $1.62 | $1.62
Resistors (8.5k) | R5 | Resistors (8.5k) | 1 | n/a | Mouser | $0.10 | $0.10
Resistors (255) | R6 | Resistors (255) | 1 | n/a | Mouser | $0.10 | $0.10
Resistors (105) | R7 | Resistors (105) | 1 | n/a | Mouser | $0.10 | $0.10
Capacitor (120p) | C1 | Capacitor (120p) | 1 | n/a | Digikey | $21.32 | $21.32
Capacitor (18p) | C2 | Capacitor (18p) | 1 | n/a | Digikey | $14.34 | $14.34
Capacitor (6.8p) | C3 | Capacitor (6.8p) | 2 | n/a | Digikey | $14.34 | $28.68
Capacitor (3.3p) | C4 | Capacitor (3.3p) | 1 | n/a | Digikey | $15.50 | $15.50
Capacitor (2.2p) | C5 | Capacitor (2.2p) | 1 | n/a | Digikey | $1.50 | $1.50
Capacitor (1.5p) | C6 | Capacitor (1.5p) | 1 | n/a | Digikey | $1.50 | $1.50
Capacitor (1.0p) | C7 | Capacitor (1.0p) | 1 | n/a | Digikey | $1.50 | $1.50
Capacitor (0.8p) | C8 | Capacitor (0.8p) | 1 | n/a | Digikey | $0.80 | $0.80
Capacitor (12p) | C9 | Capacitor (12p) | 1 | n/a | Digikey | $14.34 | $14.34

Capacitor (0.1u) | C10 | Capacitor (0.1u) | 1 | n/a | Sparkfun | $0.95 | $0.95
Capacitor (10n/0.01u) | C11 | Capacitor (10n/0.01u) | 1 | n/a | Sparkfun | $0.95 | $0.95
Zener Diode (300 V) | D1 | Zener Diode (300 V) | 6 | n/a | Mouser | $12.67 | $76.02
Zener Diode (270 V) | D2 | Zener Diode (270 V) | 2 | n/a | Mouser | $0.30 | $0.60
SMA Connector | J1 | SMA Connector | 1 | n/a | Mouser | $3.07 | $3.07
Transformer | T1 | Transforme r | 1 | n/a | Digikey | $3.92 | $3.92
PCB | PCB1 | Printed Circuit Board | 1 | n/a | JLCPCB | $7.40 | $7.40
Metal Probe | PRB1 | 316L Stainless Steel Rods Wire Diameter 2mm, length 0.5m | 1 | 316L Stainless Steel | Ethionec | $6.99 | $6.99

Total Prototyping Cost (Probe and Generator): $427.32

Data Sheet or MDS

Part Name | Unique Identifying Number | Datasheet
Avalanche Transistor | TR1 | https://www.mouser.com/datasheet/2/115/FMMT415-46058.pdf
DC-DC Converter | CONV1 | https://www.picoelectronics.com/node/13287
Zener Diode (300 V) | D1 | https://www.mouser.com/datasheet/2/268/SA5_37-1592261.pdf
Zener Diode (270 V) | D2 | https://www.mouser.com/datasheet/2/308/MM5Z4678T1_D-18 11647.pdf (https://www.mouser.com/datasheet/2/308/MM5Z4678T1_D-1811647.pdf)
Transformer | T1 | https://media.digikey.com/pdf/Data%20Sheets/Pulse%20PDFs/
LAN%20Isolation%20Transformer%20Catalog.pdf (https://media.digikey.com/pdf/Data%20Sheets/Pulse%20PDFs/LAN%20Isolation%20Transformer%20Catalog.pdf)
Metal Probe | PRB1

https://www.metalshims.com/t-316-Stainless-Steel-technical-da ta-sheet.aspx (https://www.metalshims.com/t-316-Stainless-Steel-technical-data-sheet.aspx)

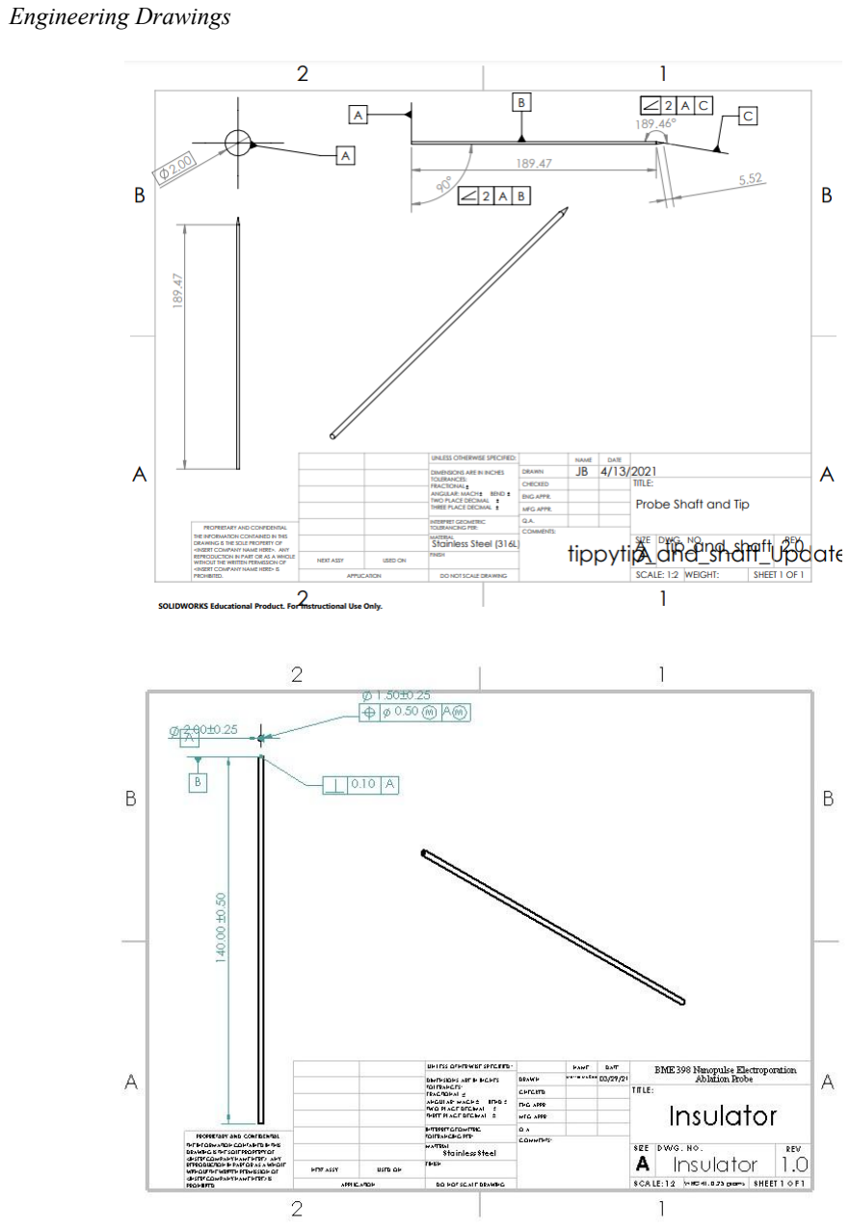
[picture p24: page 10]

Engineering Drawings

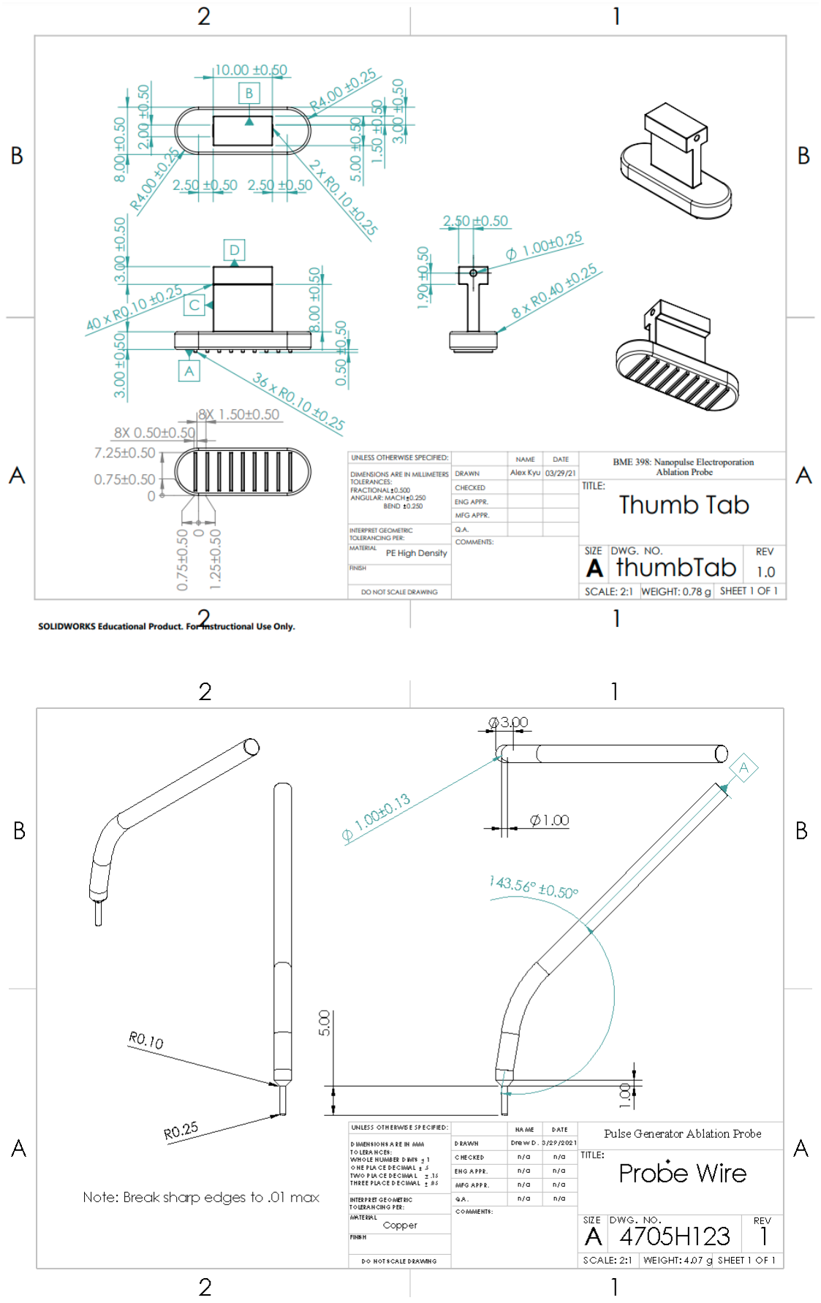
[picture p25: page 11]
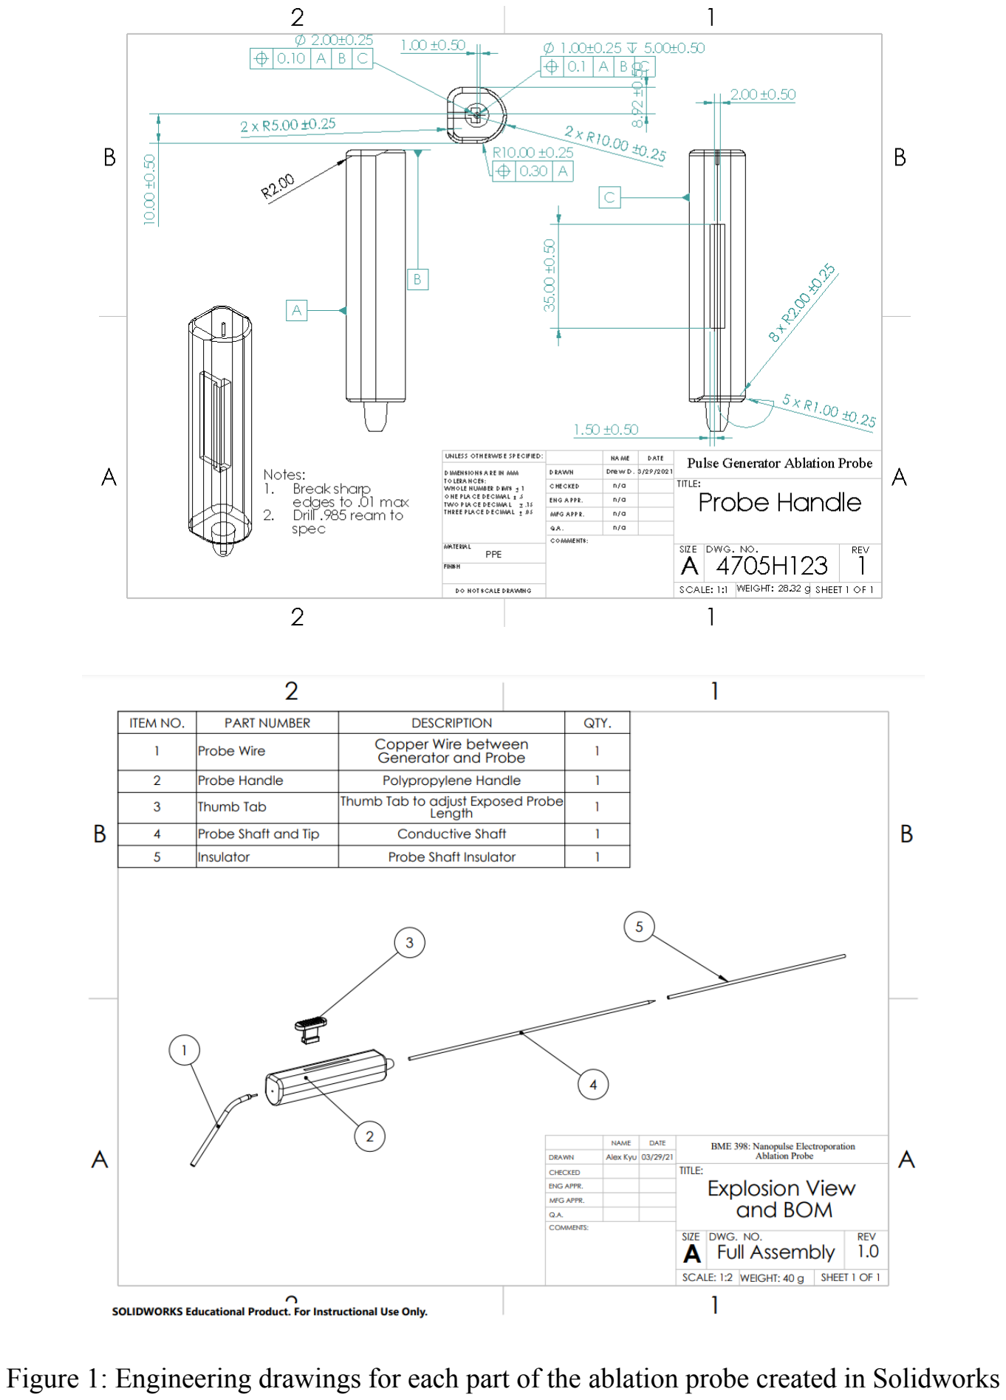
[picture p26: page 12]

Figure 1: Engineering drawings for each part of the ablation probe created in Solidworks

CNC Milling: Probe Tip

Tool Crib:

Main Removal of Material | T01 - 6mm Flat End
Shaping Probe Tip | T07 - 4mm Ball Nose

Results:

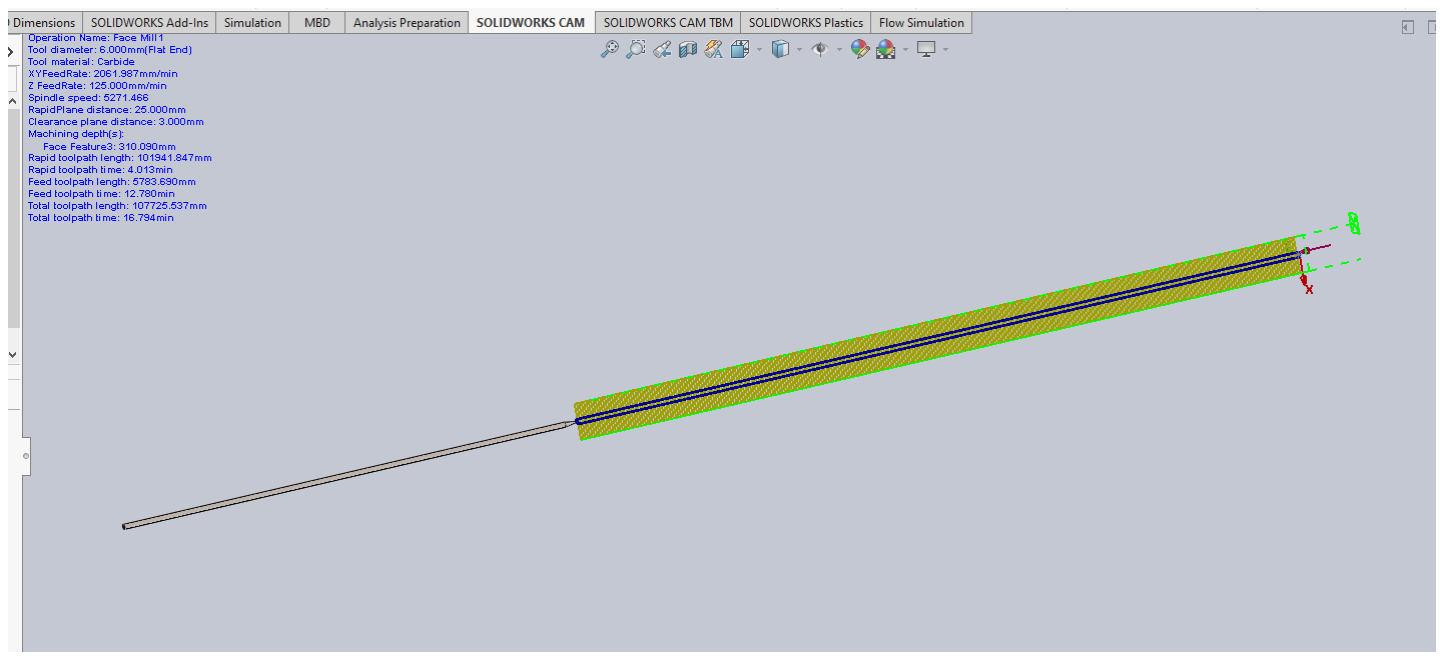
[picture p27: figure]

Figure 2: the CNC milled tip of the ablation probe

G-code: see attached

Pulse Generator PCB

See attached schematic, board and gerber files.

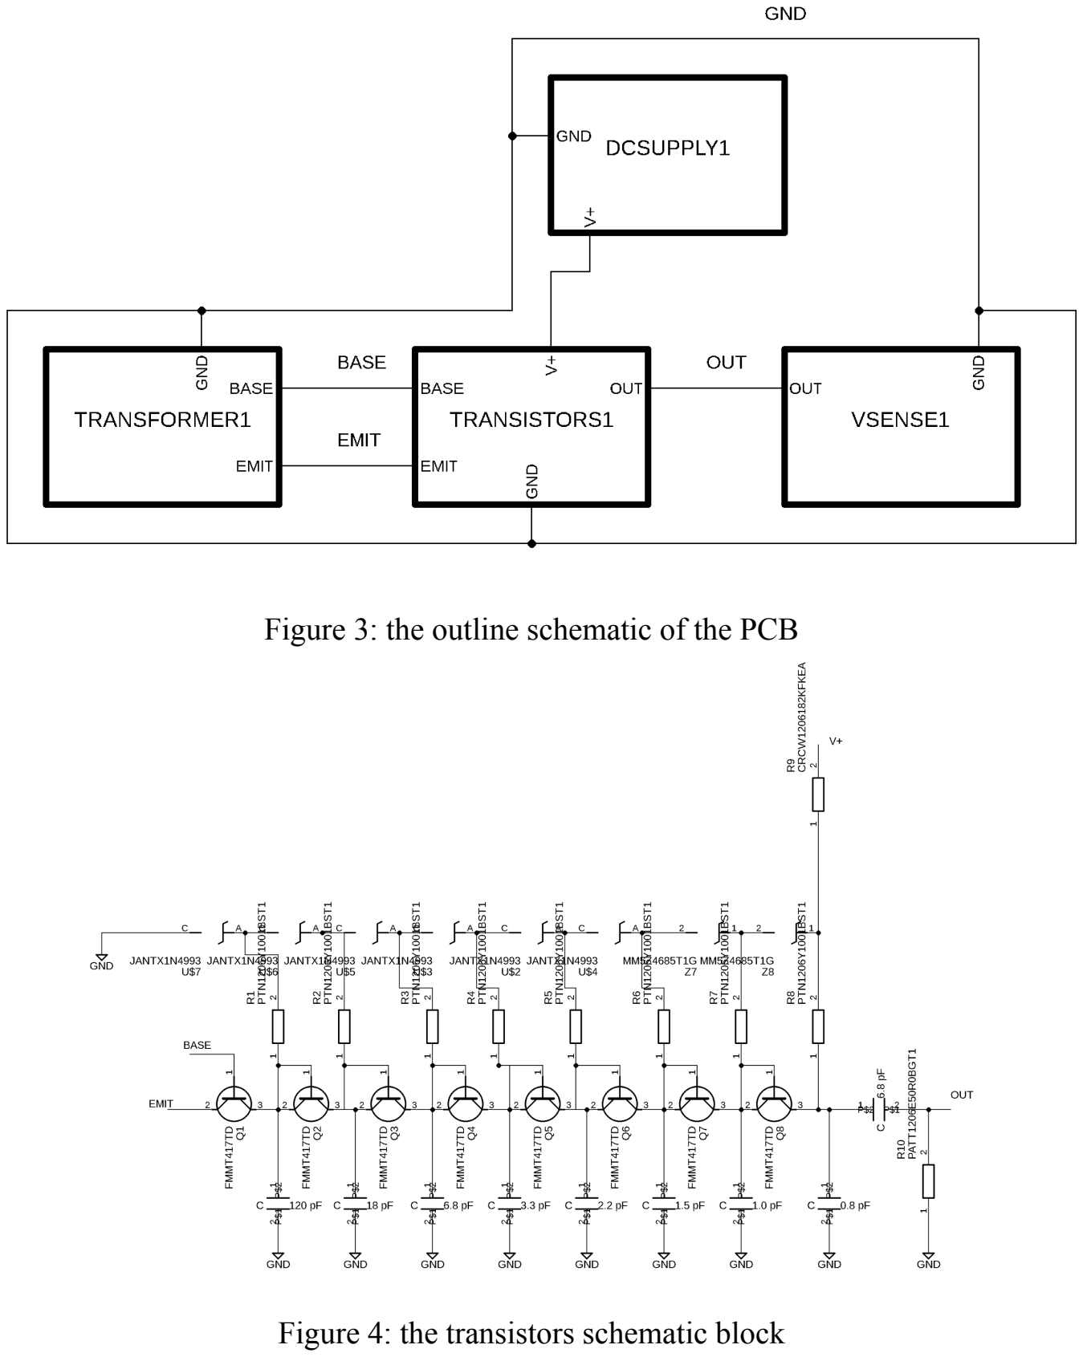
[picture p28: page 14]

Figure 3: the outline schematic of the PCB

Figure 4: the transistors schematic block

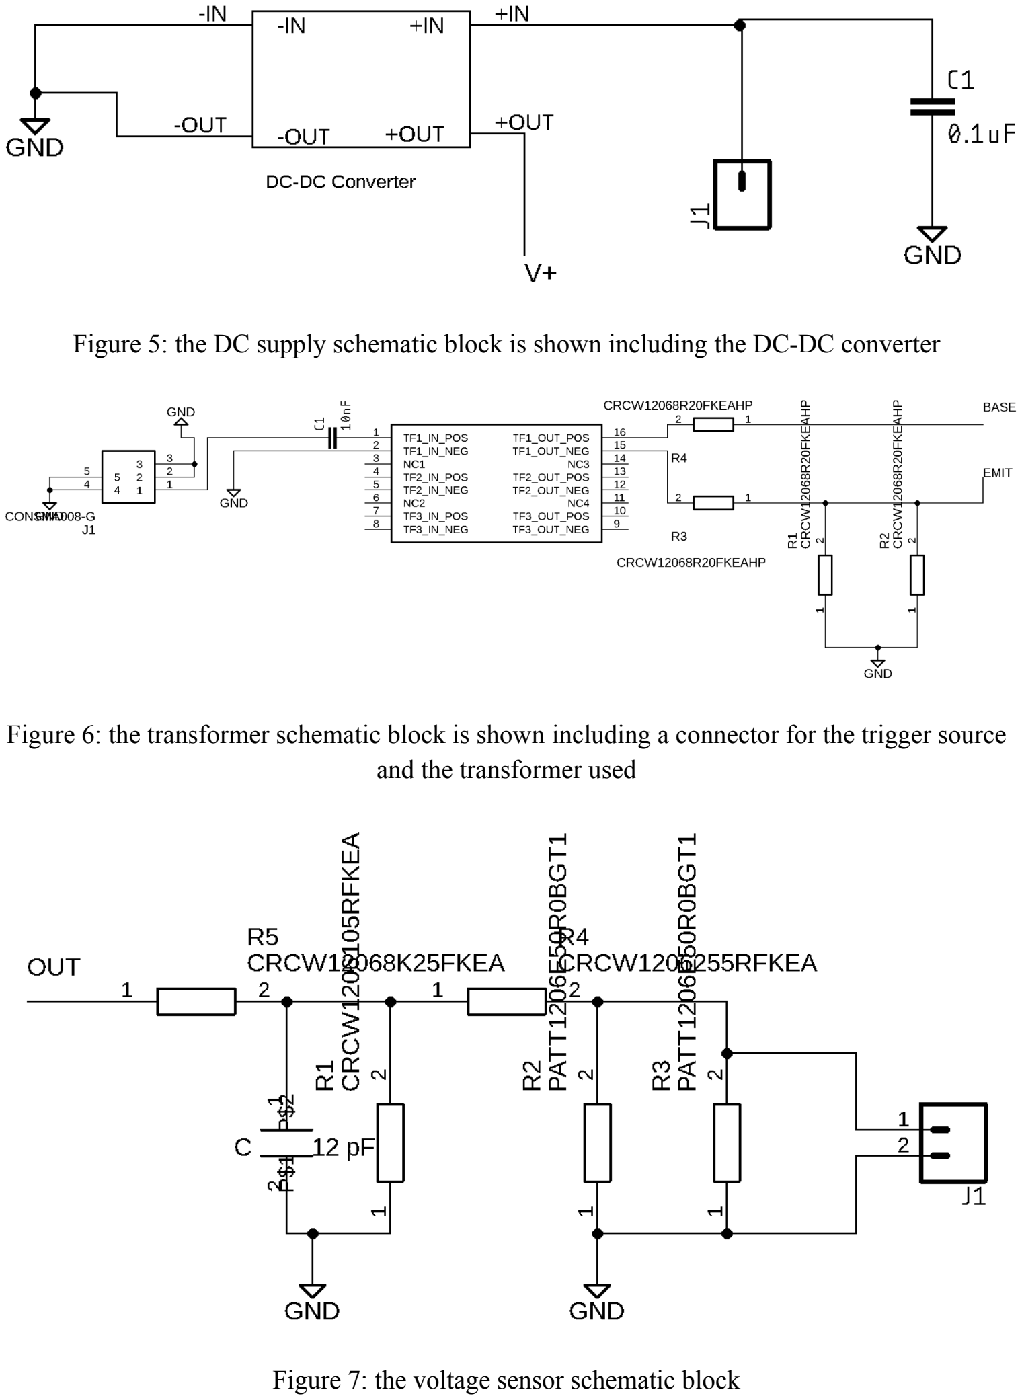
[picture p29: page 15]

Figure 5: the DC supply schematic block is shown including the DC-DC converter

Figure 6: the transformer schematic block is shown including a connector for the trigger source and the transformer used

Figure 7: the voltage sensor schematic block


Figure 8: the PCB board file highlighting the placement of each part

Verification/Validation
Unique Identifying Number: VV1 Revision Number: 1
Page Number: 3
Acceptance Status: Accepted

Quality Engineer Signature:

Work Breakdown - contribution from each team member

Alex and Drew designed the circuit in Multisim and calculated results from the simulation, providing 50% of work each. Bevin, Jeff and Mattie worked on the final paper deliverable while Alex and Drew completed the verification/validation document.

Verification/Validation

Using Multisim software, the nanosecond pulse generator circuit was modeled as shown in figure 1 and simulated with a transient response of time step 0.1 ns. The waveform produced was analyzed and the peak voltage and rise time of the output waves were recorded. This analysis was performed for varying voltage peaks of the trigger source input to the circuit while keeping a constant rise time of 0.5 ns. While spice code for avalanche transistors was downloaded, use of the code for the transistor component did not yield a pulse wave. Accordingly, the bipolar junction transistor (BJT) NPN transistor was used to model the avalanche transistor. This transistor provided a conservative estimate of the circuit as the transistor lacked the quick response of the avalanche transistors. The DC power supply block, which consisted of a 8-14.5 VDC power supply followed by a DC-DC converter, was simplified as a 2.5 kV voltage source in the simulation. The transformer was modeled with no leakage inductance or resistance; the core was modeled as non-ideal with a flux of 250uWb * tanh(.2*i) where “i” was the magnetizing inductance current.

While the results of the simulation didn’t meet the desired specifications, it did confirm that the project is plausible. With the use of Avalanche Transistors and the right components, this circuit should be able to produce the desired waveforms. Unfortunately, with the limitations of Multisim and inability to fully model the components, these waveforms could not be reproduced at the magnitude required for our device, despite simplifying the circuit to only two transistor stages. The results shown below are from the circuit schematic with all eight transistor stages (Figure 1).

However, a desired waveform was generated using switches instead of transistors, demonstrating that given a working model of the desired Avalanche Transistor, this simulation should produce the correct output voltage. Furthermore, other components may have an influence in the results too. Results for varying trigger source voltages are shown below, demonstrating that higher trigger source voltages, decreased rise time and increased peak pulse voltages (Figure 2, 3). The simulation for the pulse with a 5V trigger source is also shown below. A relatively low rise time of 5.5352 nanoseconds is shown, which could be further improved by the use of Avalanche transistors which have subnanosecond rise times (Figure 4).

Table 1: Multisim Parameters

Parameters | Value
Trigger Source Initial Value | 0 V
Trigger Source Pulse Value | 5 V
Trigger Source Rise Time | 0.5 ns
Trigger Source Fall Time | 1 ns
Trigger Source Pulse Width | 5 us
Period | 1 ms
Transformer Non-ideal Core | Flux = 250u*tanh(0.2*i)
Transformer Leakage Inductance | 0 H
Transformer Coil Resistances | 0 Ω
Transformer Coil Turns | 4:4
Simulation Type | Transient Analysis
Initial Conditions | Set to Zero
Maximum Time Step Size | 0.1 ns
Initial Time Step Size | 0.1 ns

Simulation Results:


Figure 1: Multisim Circuit Schematic

Figure 2: Simulation Results comparing Rise Time of the Pulse with changing Trigger Source Voltages.

Figure 3: Simulation Results comparing Peak Pulse Voltage with changing Trigger Source Voltages.


Figure 4: Simulation Results with a 5V Trigger Source. The Rise time was 5.5352 nanoseconds and the Peak Pulse Voltage was 2.0838 V.

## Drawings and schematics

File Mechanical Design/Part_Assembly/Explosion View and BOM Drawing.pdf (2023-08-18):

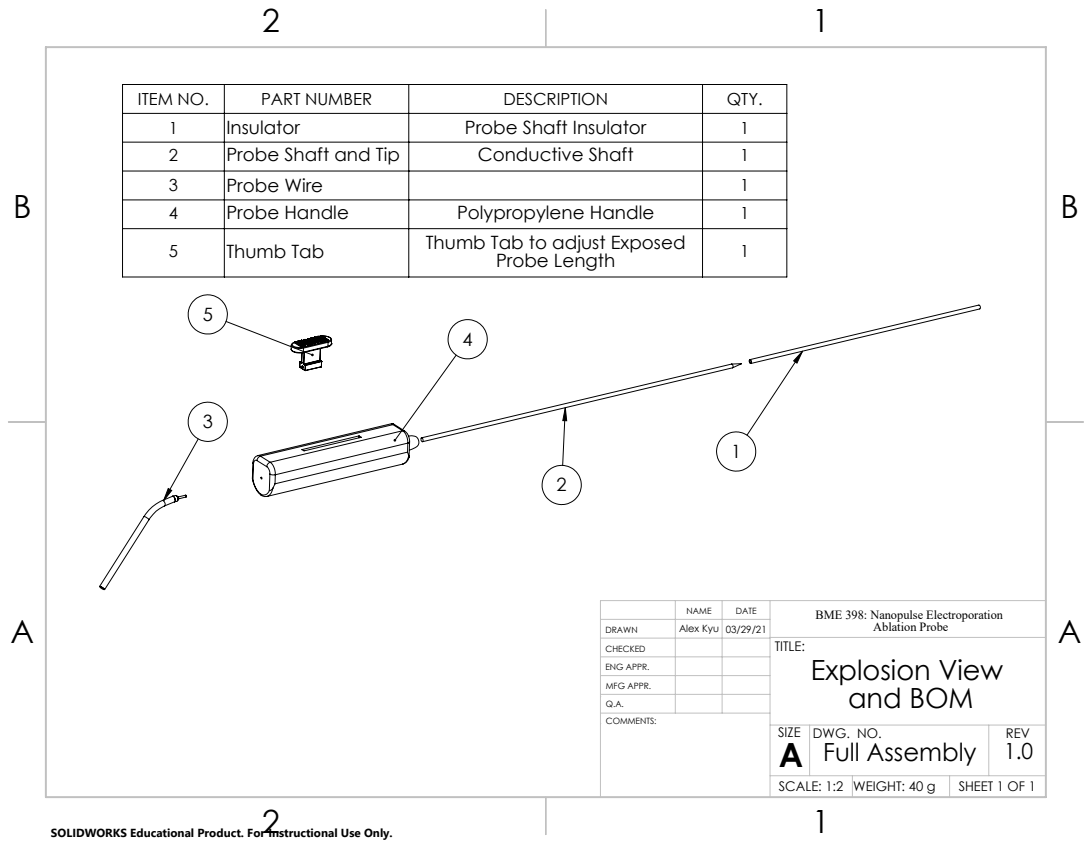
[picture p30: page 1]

ITEM NO. | PART NUMBER | DESCRIPTION | QTY.
1 | Insulator | Probe Shaft Insulator | 1
2 | Probe Shaft and Tip | Conductive Shaft | 1
3 | Probe Wire | | 1
4 | Probe Handle | Polypropylene Handle | 1
5 | Thumb Tab | Thumb Tab to adjust Exposed Probe Length | 1

NAME | DATE | BME 398: Nanopulse Electroporation Ablation Probe
CHECKED | | | TITLE: Explosion View and BOM

DRAWN | Alex Kyu | 03/29/21

ENG APPR.
MFG APPR.
Q.A.

SIZE A | DWG. NO. Full Assembly | REV 1.0

SCALE: 1:2 | WEIGHT: 40 g | SHEET 1 OF 1

SOLIDWORKS Educational Product. For Instructional Use Only.

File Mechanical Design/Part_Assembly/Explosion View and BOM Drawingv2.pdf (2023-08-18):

B

B

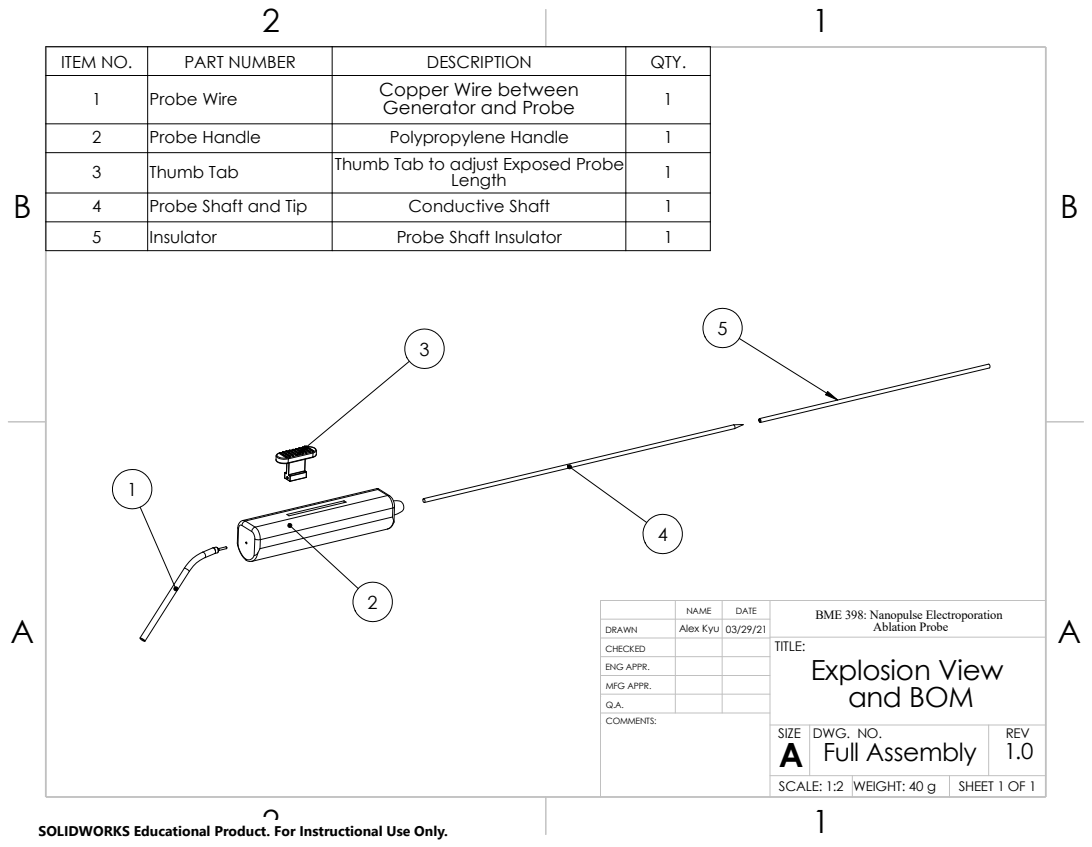
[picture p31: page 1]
COMMENTS:

ITEM NO. | PART NUMBER | DESCRIPTION | QTY.
1 | Probe Wire | Copper Wire between Generator and Probe | 1

2 | Probe Handle | Polypropylene Handle | 1
3 | Thumb Tab | Thumb Tab to adjust Exposed Probe Length | 1

4 | Probe Shaft and Tip | Conductive Shaft | 1
5 | Insulator | Probe Shaft Insulator | 1

NAME | DATE | BME 398: Nanopulse Electroporation Ablation Probe

DRAWN | Alex Kyu | 03/29/21
CHECKED | | | TITLE: Explosion View and BOM

ENG APPR.
MFG APPR.
Q.A.

SIZE A Full Assembly | DWG. NO. | REV 1.0

SCALE: 1:2 | WEIGHT: 40 g | SHEET 1 OF 1

SOLIDWORKS Educational Product. For Instructional Use Only.

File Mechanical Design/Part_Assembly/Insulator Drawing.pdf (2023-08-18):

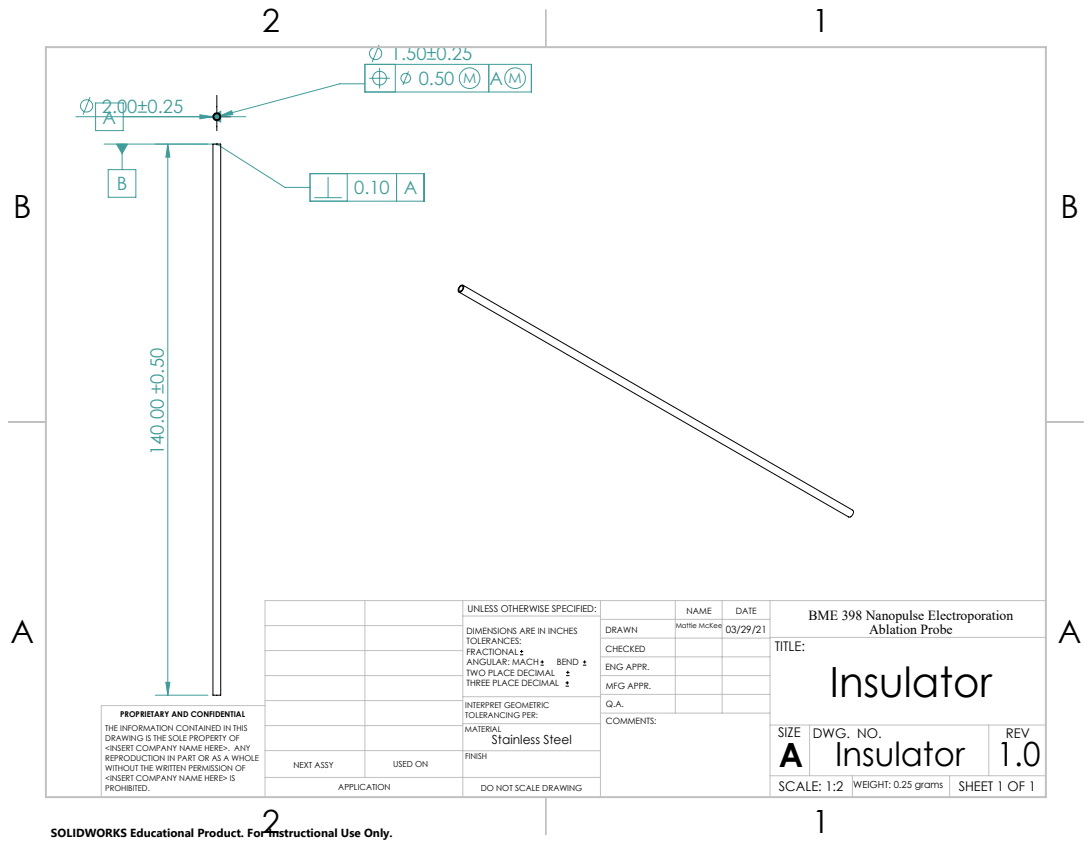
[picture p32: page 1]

UNLESS OTHERWISE SPECIFIED: | | NAME | DATE | BME 398 Nanopulse Electroporation Ablation Probe
CHECKED | | | TITLE: Insulator

DIMENSIONS ARE IN INCHES TOLERANCES: FRACTIONAL ANGULAR: MACH BEND TWO PLACE DECIMAL THREE PLACE DECIMAL | DRAWN | | 03/29/21 Mattie McKee

ENG APPR.
MFG APPR.

INTERPRET GEOMETRIC TOLERANCING PER: | Q.A.
MATERIAL Stainless Steel | | SIZE A | DWG. NO. Insulator | REV 1.0

PROPRIETARY AND CONFIDENTIAL
THE INFORMATION CONTAINED IN THIS
DRAWING IS THE SOLE PROPERTY OF
<INSERT COMPANY NAME HERE>. ANY
REPRODUCTION IN PART OR AS A WHOLE
WITHOUT THE WRITTEN PERMISSION OF
<INSERT COMPANY NAME HERE> IS
PROHIBITED.

NEXT ASSY | USED ON | FINISH

APPLICATION | DO NOT SCALE DRAWING | | SCALE: 1:2 | WEIGHT: 0.25 grams | SHEET 1 OF 1

SOLIDWORKS Educational Product. For Instructional Use Only.

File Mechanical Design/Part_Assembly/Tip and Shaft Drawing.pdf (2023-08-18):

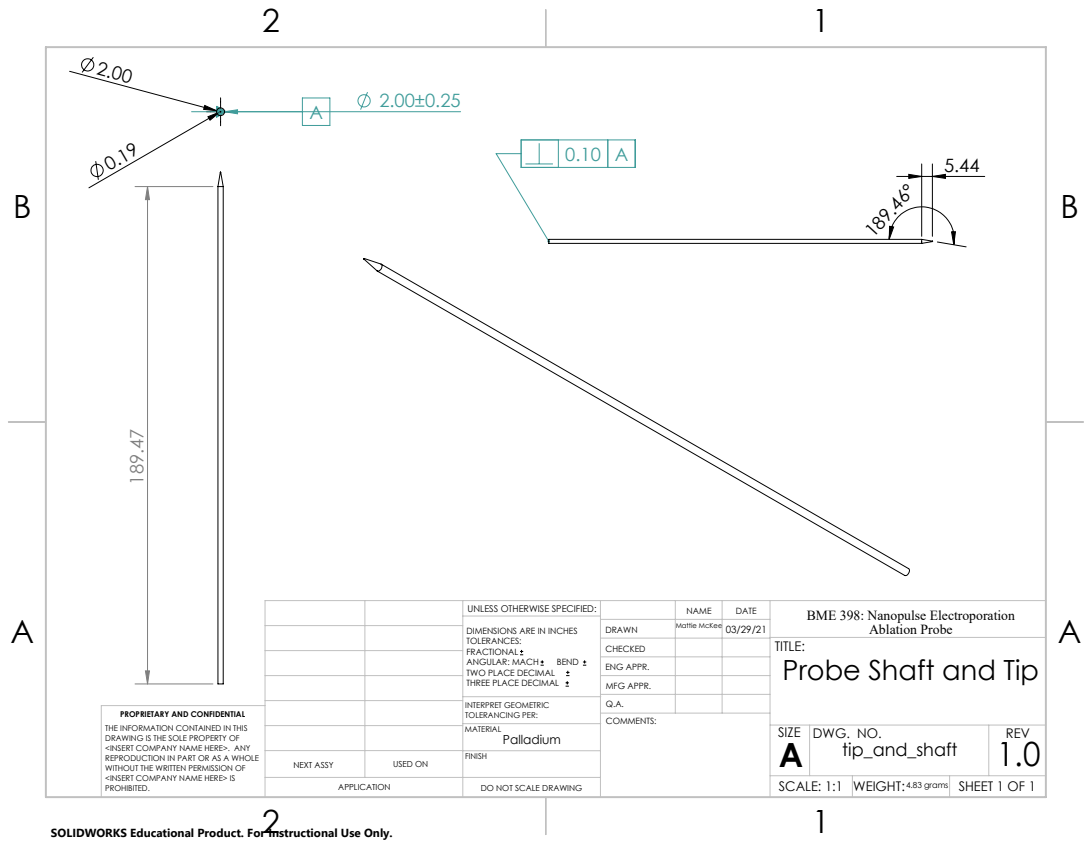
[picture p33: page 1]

UNLESS OTHERWISE SPECIFIED: | | NAME | DATE | BME 398: Nanopulse Electroporation Ablation Probe
DIMENSIONS ARE IN INCHES TOLERANCES: FRACTIONAL ANGULAR: MACH BEND TWO PLACE DECIMAL THREE PLACE DECIMAL | DRAWN | Mattie McKee | 03/29/21

CHECKED | | | TITLE: Probe Shaft and Tip

ENG APPR.
MFG APPR.

INTERPRET GEOMETRIC TOLERANCING PER: | Q.A.
MATERIAL Palladium | | SIZE A | DWG. NO. tip_and_shaft | REV 1.0

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

NEXT ASSY | USED ON | FINISH

APPLICATION | DO NOT SCALE DRAWING | | SCALE: 1:1 | WEIGHT: 4.83 grams | SHEET 1 OF 1

SOLIDWORKS Educational Product. For Instructional Use Only.

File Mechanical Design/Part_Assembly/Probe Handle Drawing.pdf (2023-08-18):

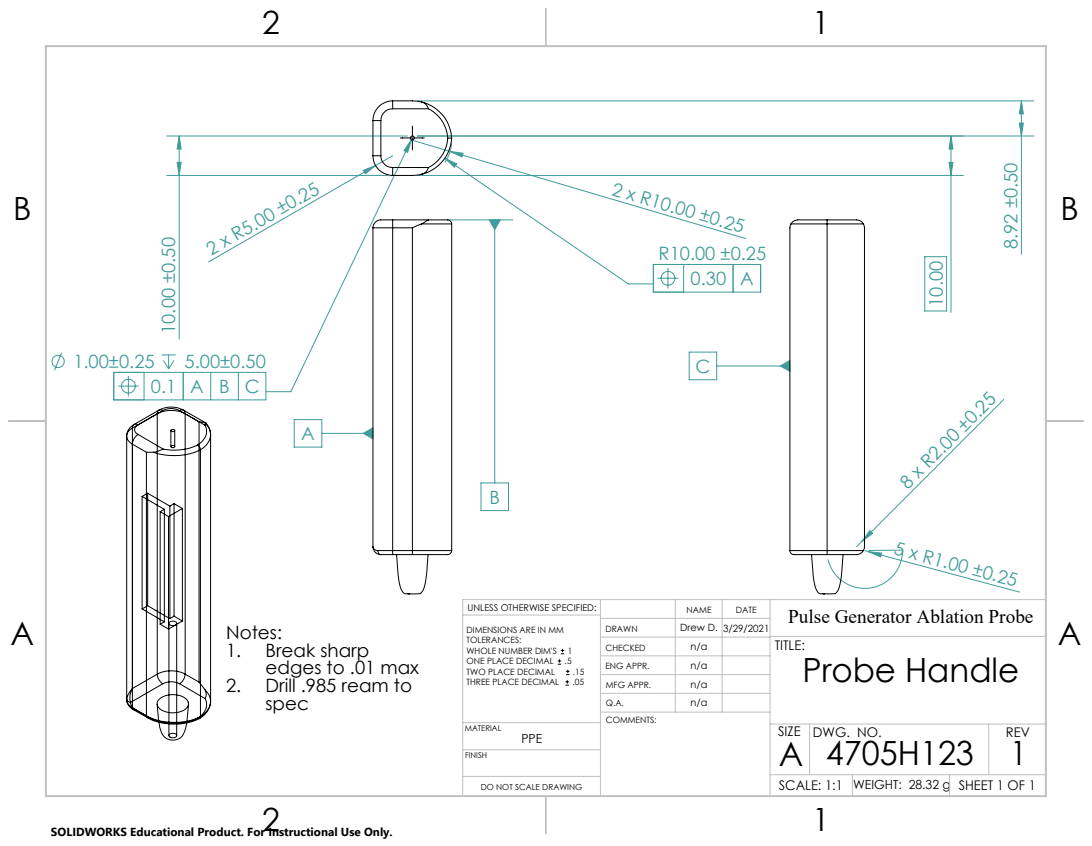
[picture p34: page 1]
SHEET 1 OF 1; SCALE: 1:1; WEIGHT: 28.32 g; DWG. NO.; REV

UNLESS OTHERWISE SPECIFIED: | | | DATE | Pulse Generator Ablation Probe NAME
DIMENSIONS ARE IN MM TOLERANCES: WHOLE NUMBER DIM'S 1 ONE PLACE DECIMAL .5 TWO PLACE DECIMAL .15 THREE PLACE DECIMAL .05 | DRAWN | Drew D. | 3/29/2021

Notes:
1. Break sharp
edges to .01 max
2. Drill .985 ream to
spec

CHECKED | n/a | | TITLE: Probe Handle
ENG APPR. | n/a
MFG APPR. | n/a
Q.A. | n/a

DO NOT SCALE DRAWING

SOLIDWORKS Educational Product. For Instructional Use Only.

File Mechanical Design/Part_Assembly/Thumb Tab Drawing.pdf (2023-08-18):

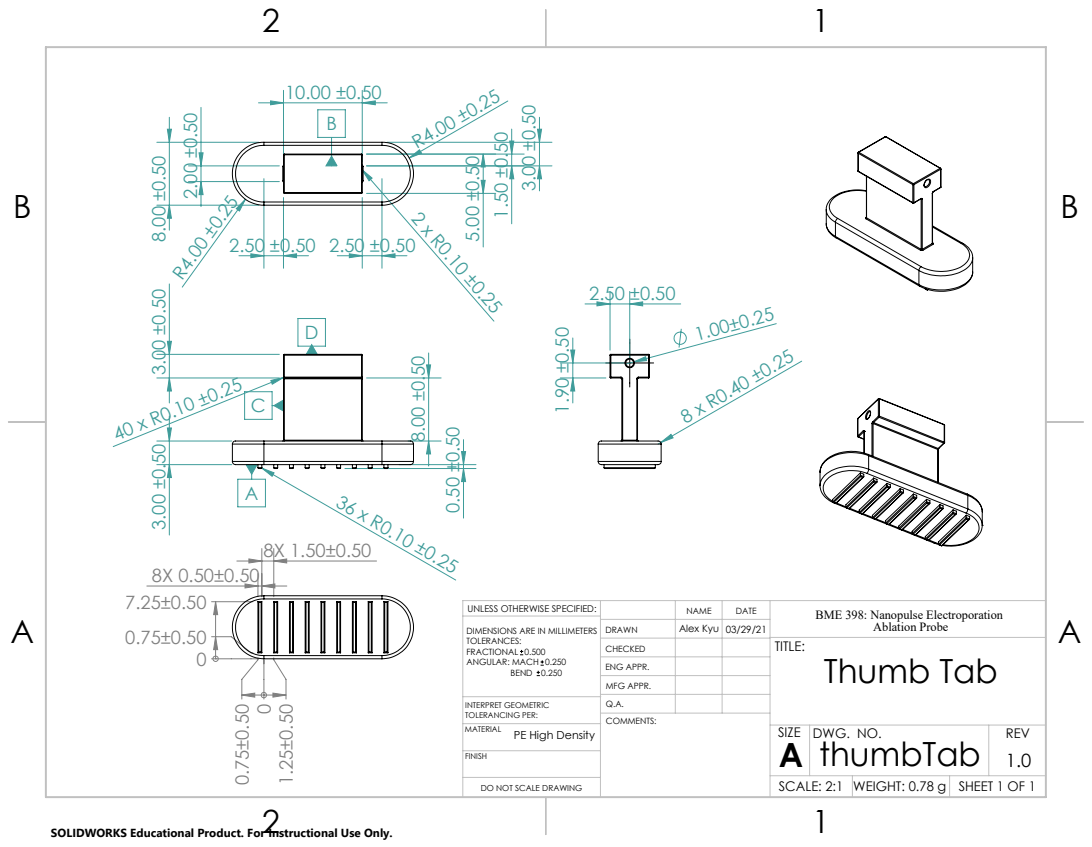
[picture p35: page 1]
SHEET 1 OF 1; SCALE: 2:1; WEIGHT: 0.78 g; DWG. NO.; REV

UNLESS OTHERWISE SPECIFIED: | | NAME | DATE | BME 398: Nanopulse Electroporation Ablation Probe
DIMENSIONS ARE IN MILLIMETERS TOLERANCES: FRACTIONAL 0.500 ANGULAR: MACH 0.250 BEND 0.250 | DRAWN | Alex Kyu | 03/29/21

CHECKED | | | TITLE: Thumb Tab

ENG APPR.
MFG APPR.

INTERPRET GEOMETRIC TOLERANCING PER: | Q.A.

PE High Density

DO NOT SCALE DRAWING

SOLIDWORKS Educational Product. For Instructional Use Only.

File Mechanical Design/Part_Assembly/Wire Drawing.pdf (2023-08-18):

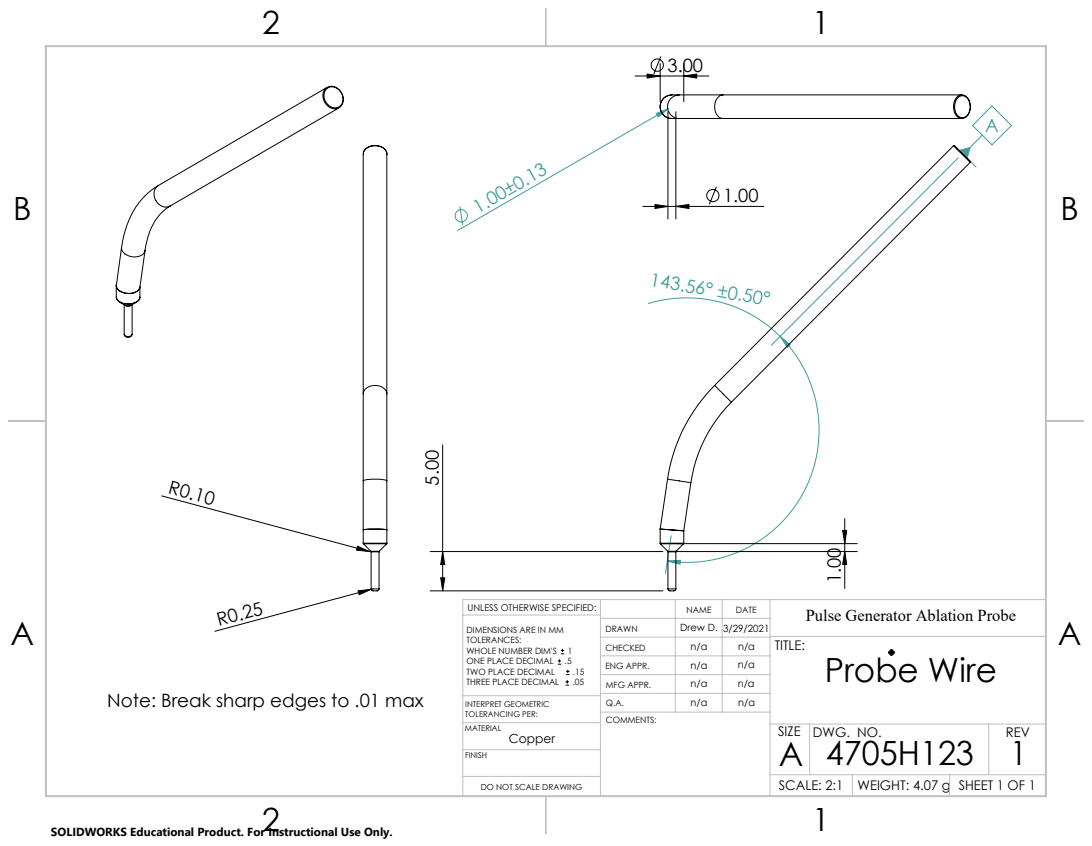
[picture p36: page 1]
SHEET 1 OF 1; SCALE: 2:1; WEIGHT: 4.07 g; DWG. NO.; REV

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

CHECKED | n/a | n/a | TITLE: Probe Wire
ENG APPR. | n/a | n/a
MFG APPR. | n/a | n/a

Note: Break sharp edges to .01 max

INTERPRET GEOMETRIC TOLERANCING PER: | Q.A. | n/a | n/a

DO NOT SCALE DRAWING

SOLIDWORKS Educational Product. For Instructional Use Only.

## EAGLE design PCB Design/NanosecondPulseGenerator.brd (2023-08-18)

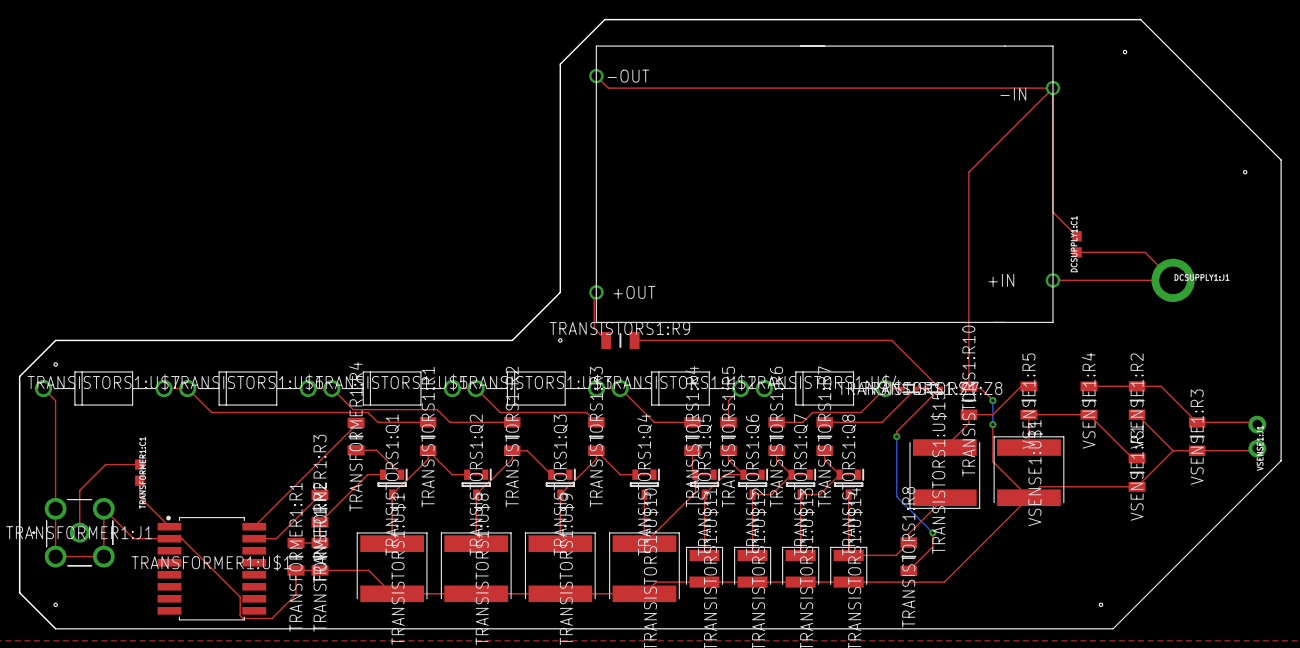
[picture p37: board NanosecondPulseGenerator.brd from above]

Board: 2 copper layers, 133.3 x 64.4 mm, 52 parts (0 on the bottom side), 28 nets.

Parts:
DCSUPPLY1:C1: 0.1uF; 0603
DCSUPPLY1:J1: SNAP-FEMALE
DCSUPPLY1:U$1: DC-DCCONVERTER; DC-CONVERTER
TRANSFORMER1:C1: 10nF; 0603
TRANSFORMER1:J1: CONSMA008-G; CONSMA008G
TRANSFORMER1:R1, TRANSFORMER1:R2, TRANSFORMER1:R3, TRANSFORMER1:R4: CRCW12068R20FKEAHP; RESC3116X65N
TRANSFORMER1:U$1: TX1:1_QUAD; SOIC127P1067X508-16N
TRANSISTORS1:Q1, TRANSISTORS1:Q2, TRANSISTORS1:Q3, TRANSISTORS1:Q4, TRANSISTORS1:Q5, TRANSISTORS1:Q6, TRANSISTORS1:Q7, TRANSISTORS1:Q8: FMMT417TD; SOT96P240X110-3N
TRANSISTORS1:R1, TRANSISTORS1:R2, TRANSISTORS1:R3, TRANSISTORS1:R4, TRANSISTORS1:R5, TRANSISTORS1:R6, TRANSISTORS1:R7, TRANSISTORS1:R8: PTN1206Y1001BST1; RESC3216X84N
TRANSISTORS1:R9: CRCW1206182KFKEA; RESC3216X60N
TRANSISTORS1:R10: PATT1206E50R0BGT1; RESC3216X46N
TRANSISTORS1:U$1: CAP_120PF; CAPCP5963X368N
TRANSISTORS1:U$2, TRANSISTORS1:U$3, TRANSISTORS1:U$4, TRANSISTORS1:U$5, TRANSISTORS1:U$6, TRANSISTORS1:U$7: JANTX1N4993; DIOAD1274W101L533D349B
TRANSISTORS1:U$8: CAP_18PF; CAPCP5963X368N
TRANSISTORS1:U$9, TRANSISTORS1:U$15: CAP_6.8PF; CAPCP5963X368N
TRANSISTORS1:U$10: CAP_3.3PF; CAPCP5963X368N
TRANSISTORS1:U$11: CAP_2.2PF; CAPCP2927X200N
TRANSISTORS1:U$12: CAP_1.5PF; CAPCP2927X178N
TRANSISTORS1:U$13: CAP_1.0PF; CAPCP2927X178N
TRANSISTORS1:U$14: CAP_0.8PF; CAPCP2927X178N
TRANSISTORS1:Z7, TRANSISTORS1:Z8: MM5Z4685T1G; SODFL1608X70N
VSENSE1:J1: 1X02_NO_SILK
VSENSE1:R1: CRCW1206105RFKEA; RESC3216X60N
VSENSE1:R2, VSENSE1:R3: PATT1206E50R0BGT1; RESC3216X46N
VSENSE1:R4: CRCW1206255RFKEA; RESC3216X60N
VSENSE1:R5: CRCW12068K25FKEA; RESC3216X60N
VSENSE1:U$1: CAP_12PF; CAPCP5963X368N

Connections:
BASE: TRANSFORMER1:R4.1, TRANSISTORS1:Q1.1
DCSUPPLY1:N$1: DCSUPPLY1:C1.1, DCSUPPLY1:J1.1, DCSUPPLY1:U$1.+IN
EMIT: TRANSFORMER1:R1.2, TRANSFORMER1:R2.2, TRANSFORMER1:R3.1, TRANSISTORS1:Q1.2
GND: DCSUPPLY1:C1.2, DCSUPPLY1:U$1.-IN, DCSUPPLY1:U$1.-OUT, TRANSFORMER1:J1.2, TRANSFORMER1:J1.3, TRANSFORMER1:J1.4, TRANSFORMER1:J1.5, TRANSFORMER1:R1.1, TRANSFORMER1:R2.1, TRANSFORMER1:U$1.2, TRANSISTORS1:R10.1, TRANSISTORS1:U$1.2, TRANSISTORS1:U$7.C, TRANSISTORS1:U$8.2, TRANSISTORS1:U$9.2, TRANSISTORS1:U$10.2, TRANSISTORS1:U$11.2, TRANSISTORS1:U$12.2, TRANSISTORS1:U$13.2, TRANSISTORS1:U$14.2, VSENSE1:J1.2, VSENSE1:R1.1, VSENSE1:R2.1, VSENSE1:R3.1, VSENSE1:U$1.2
unnamed: DCSUPPLY1:U$1.+OUT, TRANSISTORS1:R9.2
OUT: TRANSISTORS1:R10.2, TRANSISTORS1:U$15.2, VSENSE1:R5.1
TRANSFORMER1:N$1: TRANSFORMER1:R4.2, TRANSFORMER1:U$1.16
TRANSFORMER1:N$2: TRANSFORMER1:C1.1, TRANSFORMER1:J1.1
TRANSFORMER1:N$3: TRANSFORMER1:C1.2, TRANSFORMER1:U$1.1
TRANSFORMER1:N$4: TRANSFORMER1:R3.2, TRANSFORMER1:U$1.15
TRANSISTORS1:N$1: TRANSISTORS1:Q1.3, TRANSISTORS1:Q2.1, TRANSISTORS1:Q2.2, TRANSISTORS1:R1.1, TRANSISTORS1:U$1.1
TRANSISTORS1:N$2: TRANSISTORS1:R8.2, TRANSISTORS1:R9.1, TRANSISTORS1:Z8.1
TRANSISTORS1:N$4: TRANSISTORS1:Q4.3, TRANSISTORS1:Q5.1, TRANSISTORS1:Q5.2, TRANSISTORS1:R4.1, TRANSISTORS1:U$10.1
TRANSISTORS1:N$8: TRANSISTORS1:R3.2, TRANSISTORS1:U$3.C, TRANSISTORS1:U$5.A
TRANSISTORS1:N$9: TRANSISTORS1:Q2.3, TRANSISTORS1:Q3.1, TRANSISTORS1:Q3.2, TRANSISTORS1:R2.1, TRANSISTORS1:U$8.1
TRANSISTORS1:N$10: TRANSISTORS1:Q3.3, TRANSISTORS1:Q4.1, TRANSISTORS1:Q4.2, TRANSISTORS1:R3.1, TRANSISTORS1:U$9.1
TRANSISTORS1:N$12: TRANSISTORS1:Q5.3, TRANSISTORS1:Q6.1, TRANSISTORS1:Q6.2, TRANSISTORS1:R5.1, TRANSISTORS1:U$11.1
TRANSISTORS1:N$13: TRANSISTORS1:Q6.3, TRANSISTORS1:Q7.1, TRANSISTORS1:Q7.2, TRANSISTORS1:R6.1, TRANSISTORS1:U$12.1
TRANSISTORS1:N$14: TRANSISTORS1:Q7.3, TRANSISTORS1:Q8.1, TRANSISTORS1:Q8.2, TRANSISTORS1:R7.1, TRANSISTORS1:U$13.1
TRANSISTORS1:N$15: TRANSISTORS1:Q8.3, TRANSISTORS1:R8.1, TRANSISTORS1:U$14.1, TRANSISTORS1:U$15.1
TRANSISTORS1:N$16: TRANSISTORS1:R7.2, TRANSISTORS1:Z7.1, TRANSISTORS1:Z8.2
TRANSISTORS1:N$17: TRANSISTORS1:R6.2, TRANSISTORS1:U$4.A, TRANSISTORS1:Z7.2
TRANSISTORS1:N$18: TRANSISTORS1:R4.2, TRANSISTORS1:U$2.C, TRANSISTORS1:U$3.A
TRANSISTORS1:N$19: TRANSISTORS1:R2.2, TRANSISTORS1:U$5.C, TRANSISTORS1:U$6.A
TRANSISTORS1:N$20: TRANSISTORS1:R1.2, TRANSISTORS1:U$6.C, TRANSISTORS1:U$7.A
TRANSISTORS1:N$22: TRANSISTORS1:R5.2, TRANSISTORS1:U$2.A, TRANSISTORS1:U$4.C
VSENSE1:N$1: VSENSE1:J1.1, VSENSE1:R2.2, VSENSE1:R3.2, VSENSE1:R4.2
VSENSE1:N$2: VSENSE1:R1.2, VSENSE1:R4.1, VSENSE1:R5.2, VSENSE1:U$1.1

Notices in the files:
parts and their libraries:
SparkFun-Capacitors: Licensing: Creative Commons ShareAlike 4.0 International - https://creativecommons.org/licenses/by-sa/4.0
